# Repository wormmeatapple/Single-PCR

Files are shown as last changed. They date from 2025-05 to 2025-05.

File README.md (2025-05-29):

# Single-PCR
A cheap, easy to use single tube PCR thermocycler for biotech.
For Hack Club's Highway event!

<p>Polymerase-chain-reaction (PCR for short) is a vital reaction used in all sorts of biology fields. It amplifies a predetermined segment of dna, doubling it every cycle! PCR has three steps; 1. Get quite hot (95c) to split apart dna 2. Cool back down to allow little marker pieces of rna to anneal to the big, now detached dna 3. Heat back up to allow little protein machines to create more dna! This repeats 20-40 times until you have BILLIONS of copies of a specific piece of dna. This cycling is often done in very expensive, university level PCR thermocyclers that use peltier modules to heat and cool dynamically. My design does the same heating and cooling by using much cheaper components, resistive heaters and cpu fans. (Back in the day they used heated water baths!). I aim for Single-PCR to be a cheap easy PCR alternative for hobbyists. It'll be controlled by an ESP-8266 board broadcasting a control website. From the control website you can adjust cycles, monitor temperature data, abort reactions etc. Creating this vital piece of hardware would allow me to preform tons of different biohacking protocols, and if I can make it cheap enough, maybe it'll let others do the same!<p/>
  
singlepcr

|Item name|What the item is for in your project|Item source|Item price (include shipping + taxes)|Total price|
|--------|-------------------------------------|------------|-------------------------------------|------------|
|Aluminium heating block|To hold the PCR tube,and to be heated and cooled by the heating elements/cooling fans|JLCPCB CNC manufacturing|60.56+27.66 shipping|88.22|
|Heating element 2 pcs|To heat the heating block and thus the tube inside it.|https://www.aliexpress.com/item/1005007920697887.html?|2.92+9.36 shipping|12.28|
|10kΩ NTC Thermistor 10 pcs|To give temperature readings so the microcontroller knows when to heat/cool.|https://www.aliexpress.com/item/1005008177000786.html?|3.51+0 shipping|3.51|
|12V 1A wall-mounted DC power supply|Supply 12V power to the heaters and the fan.|https://www.aliexpress.com/item/1005005763465796.html?|5.08+0 shipping|5.08|
|Thermal paste|Increase thermal conductivity between heaters and heating block.|https://www.aliexpress.com/item/1005007037912738.html?|4.29+0 shipping|4.29|
|Transistors (12V)|Allow the microcontroller to control whether the fan gets power.|https://www.aliexpress.com/item/1005008370773690.html?|1.82+0 shipping|1.82|
|DC Fans 2 pcs|Blow air across the heatsink fins to cool down the heating block.|https://www.aliexpress.com/item/1005006306536871.html?|10.60+0 shipping|10.60|
|ESP control board|Read temperature data, control transistors, broadcast control website to user.|My cupboard|Free!I have some|0.00|
|**Total**||| |**125.80 AUS**/**80.60 USD**|

<br>
<br>





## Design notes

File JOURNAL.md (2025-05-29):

---
title: "Single-PCR"
author: "wormmeatapple"
description: "A tiny PCR machine designed to be cheap and easy"
created_at: "24th/5/2025"
time taken: 9 hours
---

## May 24th

> Created repo  
> Found the parts I'm going to need; heater elements and thermistors  
> Started 3d modelling based on selected parts



<p>I want to try and limit how much material is between the heaters and the tube, so I'm using a quite thin wall. I did ask people in the #cad channel what they thought of this but at time of writing I didn't get a reply</p>



<p>Heatsink fans on one side, now just to mirror them.</p>



<p>Very nice! We now have a hole for the PCR tube to go in, a hole for the thermistor, slots for the heaters and heatsinks to cool down easier. I'm not sure how well this'll be CNCed as I've never ordered a CNC part before but hopefully nothing breaks.</p>

> Time taken: about **30 mins**  
> - Modelling  
> - Researching parts

## Still May 24th

<p> Spent a ton of time researching and compiling parts. While not very technical, it's time that's very much needed. I also now know the specs of everything, so I can start writing code to control it all!</p>

> Time taken: **1 hour**
> - Compiling BOM
> - Researched all parts

## May 25th

>Started designing a wiring circuit

<p>First time ever using a pcb designer, but I'm slowly making process on the wiring schematic. I'm making it on easy-ada designer and since it technically isn't really a pcb alot of the parts I need aren't there.</p>
<p>This could maybe be a pcb? It'd be kinda small but it'd make wiring everything slightly easier? Something for me to think about.</p>
<p>Just as I was about to take a screenshot, website froze up and erased my progress. -__- I can't prove it either which sucks. Ah well, an hour wasted. Time for lunch.</p>

<br>



<p>Screenshotting more frequently this time.</p>



<p>Fans and thermistor circuit all wired up, now just the heaters.</p>



<p>Done! I'm sure I could of done it better, faster and with the proper parts, but for the first time designing a circuit like this I think I did alright. I'll send it into the highway chat and see if anyone finds an issue in it.</p>
<p>As soon as I wrote that I looked back on it and wanted to make a couple of changes, one second...</p>



<p>Much nicer. The old format made sense, but for someone who isn't as well versed in circuitry this is way easier to follow</p>

> Time taken **1h 57m**
> - Wired up all components
> - Lost an hour to a crash :sob:

<p>Got some feedback on my schematic. Mainly that I should wire the heaters in parellal and I should change the relay for a transistor.</p>



> Time taken **7m**
> - Finally learnt how to tell if something is parellal 

> Now time to code up the control side of everything
<p>My plan is to have a website that the esp8266 broadcasts and the user connects to. Once you've connected you can choose the cycle times and monitor the temperature.</p>



<p>Stupid port 6 only opens when I'm in device manager.</p>
<p>So weird, I keep getting a "permission denied" error for my com port?</p>
<p>Ohhhhh, having serial monitor open counts as a connection, so arduino ide wasn't free to flash. Everything is back to working now.</p>
<p>Just fiddled around with the code for a while before I realised it was trying to be a station not an access point. 🤦</p>



<p>Was going to take this screenshot to complaing about how it isn't working, but instead found my phone is just refusing to display the html. In other news, finally have a prototype! Now I can start drafting the other functions I need like reading temp and making a cycle.</p>

<p>Code now handles different links. Not exactly necessary as everything needed by the user is on the homepage, but is useful for AJAX (acting like I didn't learn what AJAX was today</p>

<p>Now a div in the html is updated every second with the readings from the thermistor using AJAX. Preferably I would like it to be graphed over time and overlayed on the user's requested cycle, but the only graphing option I've found relies on using an external JS libary.</p>



<p>So messy. I can't even read it.</p>

<p>That's it for today. All and all pretty efficient. Posting the arduino sketch right after I commit this.</p>

> Time taken **2h 27m**
> - Added webserver functions to controller
> - Added simple temperature function
> - AJAX to continously update page with temperature data
> - Started adding fan/heater control

## May 26th

<p>Just got three things left to do before I submit,</p>

> - Add graphing while offline
> - Add a way to specify cycles that the controller reads and then actually does
> - Overlay the temp graph and the cycle graph (probably easiest?)

<p>Gonna work on the graphing first. In my research I kept seeing people suggest the Chartly.JS library, but this doesn't work while offline. Hm</p>

<p>I think I've found a solution. I'm gonna install LittleFS on my board and than just store the js libary on my esp? I hope</p>

<p>Why won't the tool show up in the tool dropdown?</p>



<p>That's annoying. I've just spent ages (futilely) trying to get the uploader to show in the tool dropdown, but I just checked the size of chartly and it's more than the flash size. Awesome. I guess I'll have the board act as an AP and a STA so that it has wifi access. Booooo.</p>

<p>I'm deciding to temporarily put the graphing on hold and focus on the actual functionality of turning the heater and fan on and off to reach a desired temp.</p>

<p>Now that I'm making it, why is this thing website operated? It can't keep a substantial memory so it wouldn't be able to store preset cycles decided by the user or anything like that. I'll keep the webserver stuff for now, but when it's done it'll probably just be used to start the cycle and read the temp 👎</p>

<p>Actually no, the cycles will stay the same, but depending on the GC content of the dna being PCRed, denaturation has to change. So instead it'll be like a form where you input how long the denature and extension steps have to be. Honestly such a relief, I thought all my webserver shenanigans would be a waste.</p>

<p>Okay I've actually figured out a procedure that actually makes sense. When you boot up the machine you follow these steps. 1. Connect to the access point 2. Enter in your PCR settings like number of cycles, length of each phase, temp of each phase etc 3. Hit start 4. Watch the temp graph</p>



<p>I've added in a function to control the heat simply by polling the therm, if lower than the ideal heat turn on heaters, if higher turn on fans. Than I put it into the loop connected to an if statement that turns on when you submit the form of variables. All the durations and ideal temps are governed by the variables that you chose from the form. !!! It should all be good and working! Just need to fix up the html. Also sidenote I don't know the proper way to do it but why can't I just have this function be void. If it has any arguements has to return something like bruh.</p>

<p>Blank white screen on my arduino ide. Worrying.</p>

<p>Was able to press save despite the blank screen of nothing. Maybe I should make a backup...</p>



<p>Pretty simple cycle mechanic. I do wonder if the delays in the cycle() function will stop the handleclient() function from working. I guess we'll find out eventually</p>

<p>Tested out everything and it seems to work. Forms send info, info gets converted to variables, variables control cycle, cycle controls pins. I even got the pins to light up an led, so it should be all good to go! I do wonder if there's a cheaper way to get my heating block CNCed though. I'll ask highway.</p>

> Time taken
> - **3h 2m**
> - Rethought of project design
> - User data converted to cycle settings
> - cycle settings control pins

<p>Gonna submit it today, I'm scared that I'll be missing something really simple and have to wait a week before submitting again. I definitly could have made this quicker, but I always choose to do new things for these events, I suppose that's the point though.</p>

## May 29th

<p>Got some feedback from @alexren, so I thought I'd talk a little about how a typical PCR machine works in detail (I'll add a simplier version to the readme).</p>

<p>If you've read the readme of this project, you know a PCR machine's main goal is to just change the temperature of a little chemical reaction in a repeating nature. The thousand dollar ones found in universities and real labs use peltier modules, which is essentially an electric heat pump.</p>



<p>If you power it, one side gets cold and the other gets hot. Flip the polarities and the hot and cold sides switch. So, a good PCR machine has your standard heating block to allow smooth temp distribution, and then some high quality peltiers stuck to it, allowing you to switch between hot and cold preeeety quick. Now I'm not a university or million dollar biotech lab, so I've gotta use a different method. I have to do heating through a ceramic resistance based heater, and cooling through a fan and heatsink. This works fine, if slightly slower to reach the appropriate temps, because the temperature PCR occurs at is pretty warm anyway. All the fan is doing is reversing the heating process essentially. So my heater gets the heat block (and thus the PCR tube) hot, and then the fan cools it back down quicker than ambient heat loss would. There is technically one thing about a regular PCR machine that I can't emulate. Usually after a PCR reaction has finished cycling and done the final extension step, the peltiers cool it all the way down to around 4c. This is just to protect the dna since it's a pretty delicate molecule, and transforming a broken piece of dna into something is a bad idea. To combat this, if you use Single-PCR, just be there when the reaction finishes to move your dna into the freezer 👍.</p>

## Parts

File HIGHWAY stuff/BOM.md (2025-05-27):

> **Total = 81.13 AMERICAN DOLLARS**
> - 125.80 AUS

# Aluminium heating block 
<br> **60.56** + **27.66 shipping** <br> **88.22 total** If anyone knows any cheaper cnc options please contact me :sob:<br>
# Heating element 2pcs 
<br> **2.92** + **9.36 shipping** <br> **12.28 total** <br>
# 10k NTC Thermistor 10pcs 
<br> **3.51** + **0 shipping!!** <br> **3.51 total** <br>
# 12 volt 1 amp wall mounted DC power supply 
<br> **5.08** + **0 shipping!!** <br> **5.08 total** <br>
# Thermal paste 
<br> **4.29** + **0 shipping** <br> **4.29 total** <br>
# Transitors (12v) 
<br>  **1.82** + **0 shipping** <br> **1.82 total** <br>
# DC Fans 2pcs
<br> **10.60** + **0 shipping** <br> **10.60 total** <br>
# Esp control board
<br> **Free! I have some** 

<br>

<p>Prices in BOM in AUS</p>

[BOM.csv](https://github.com/user-attachments/files/20453770/BOM.csv)

<p>I wasn't sure what was meant by csv table, I hope this is okay...</p>

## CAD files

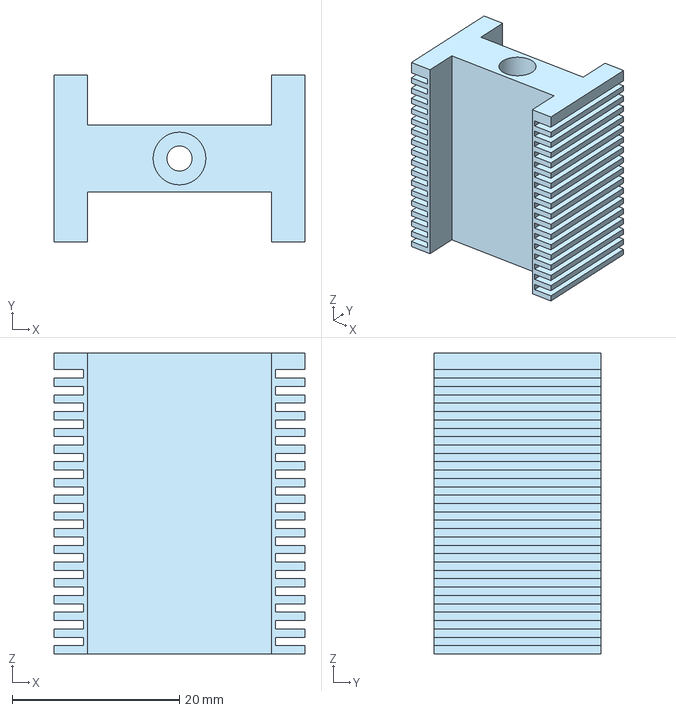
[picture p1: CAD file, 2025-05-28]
CAD stuff/singlepcrheatingblock.step
30.0 x 20.0 x 36.0 mm

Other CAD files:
singlepcrheatingblock.step
CAD stuff/singlepcrheatingblock.stl

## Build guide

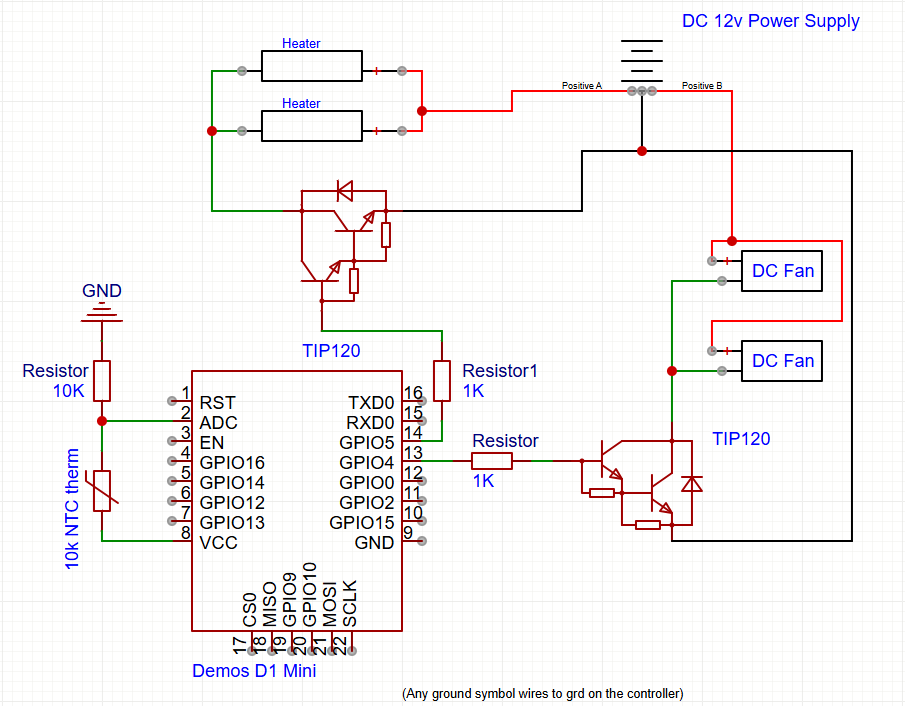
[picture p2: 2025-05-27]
WIRING stuff/wiringschematic.png

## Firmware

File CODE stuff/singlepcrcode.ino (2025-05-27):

#include <ESP8266WiFi.h>
#include <ESP8266WebServer.h>


//wifi variables
const char* ssid = "Single_PCR";
const char* password = "admin";
IPAddress local_ip(192,168,1,1);
IPAddress gateway(192,168,1,1);
IPAddress subnet(255,255,255,0);
ESP8266WebServer server(80); //port 80

//sensor variables
const int analogPin = A0;
const int resistorValue = 10000; //read therm res and change when it arrives

//pcr specific variables
bool on = false;
int extensionDur = 0;
int extensionTemp = 0;
int denatureDur = 0;
int annealDur = 0;
int annealTemp = 0;
int cycleNum = 0;


//temp control variables
const int heaterPin = D1;
const int fanPin = D2;

float read_temp()
{
  int sensorValue = analogRead(analogPin);
  float resistance = resistorValue / ((1023.0 / sensorValue) - 1.0);
  float temp = log(resistance / 10000.0) / 3950.0 + 1.0 / (25 + 273.15);
  return temp;
}

int cycle(int duration, int idealTemp)
{
  unsigned long startTime = millis();
  long elapsed = millis() - startTime;

  while (elapsed < duration)
  {
    float currentTemp = read_temp();
    if(currentTemp < idealTemp)
    {
      digitalWrite(heaterPin, HIGH);
      delay(100);
      digitalWrite(heaterPin, LOW);
    }
    else if (currentTemp > idealTemp)
    {
      digitalWrite(fanPin, HIGH);
      delay(100);
      digitalWrite(fanPin, LOW);
    }
    elapsed = millis() - startTime;
  }
  return 1;
}

//handle different links
void handle_connect()
{
  server.send(200, "text/html", SendHome());
}
void handle_data()
{
  float temp = read_temp();
  server.send(200, "text/html", String(temp));
}
void handle_start()
{
  on = true;

  if (server.hasArg("extensionDur")) {
    extensionDur = (server.arg("extensionDur").toInt()) * 10;
  }
  if (server.hasArg("extensionTemp")) {
    extensionTemp = (server.arg("extensionTemp").toInt()) * 10;
  }
  if (server.hasArg("denatureDur")) {
    denatureDur = (server.arg("denatureDur").toInt()) * 10;
  }
  if (server.hasArg("annealDur")) {
    annealDur = (server.arg("annealDur").toInt()) * 10;
  }
  if (server.hasArg("annealTemp")) {
    annealTemp = (server.arg("annealTemp").toInt()) * 10;
  }
  if (server.hasArg("cycleNum")) {
    cycleNum = server.arg("cycleNum").toInt();
  }

}
void handle_404()
{
  server.send(404, "text/html", "Send a real link dingus");
}

void setup()
{
  Serial.begin(115200);
  Serial.println();

  WiFi.softAP(ssid, password);
  WiFi.softAPConfig(local_ip, gateway, subnet);
 
  //link directory
  server.on("/", handle_connect);
  server.on("/data", handle_data);
  server.on("/start", handle_start);
  server.onNotFound(handle_404);

  server.begin();
  Serial.println("we bootin");

  pinMode(heaterPin, OUTPUT);
  pinMode(fanPin, OUTPUT);
}

void loop()
{
  server.handleClient();

  if(on)
  {
    cycle(300, 95); //inital denature
    for(int i = 0; i < cycleNum + 1; i++)
    {
      cycle(denatureDur, 95); //cycle denaturing
      cycle(annealDur, annealTemp); //cycle annealing
      cycle(extensionDur, extensionTemp); //cycle extension
    }
    cycle(300000, extensionTemp); //final extension
    on = false;
  }
}

String SendHome()
{
String html = "<!DOCTYPE html> <html>\n";
  html +="<head><meta name=\"viewport\" content=\"width=device-width, initial-scale=1.0, user-scalable=no\">\n";
  html +="<title>Single PCR</title>\n";
  html +="<style>html { font-family: Helvetica; display: inline-block; margin: 0px auto; text-align: center;}\n";
  html +="body{margin-top: 50px;} h1 {color: #444444;margin: 50px auto 30px;} h3 {color: #444444;margin-bottom: 50px;}\n";
  html +="</style>\n";
  html +="</head>\n";
  html +="<body>\n";
  html +="<h1>Single PCR</h1>\n";
  html +="<h3>Rancid inc. Making things Rancid since 1893</h3>\n";
  html +="<form action='/start'>";
  html +="Duration of extension: <input type='text' name='extensionDur'><br>";
  html +="Temperature of extension: <input type='text' name='extensionTemp'><br>";
  html +="Duration of denaturing: <input type='text' name='denatureDur'><br>";
  html +="Duration of annealing: <input type='text' name='annealDur'><br>";
  html +="Temperatur of annealing: <input type='text' name='annealTemp'><br>";
  html +="Amount of cycles: <input type='number' name='cycleNum'><br>";
  html +="<input type='submit' value='Submit'>";
  html +="</form>";
  html +="</body>\n";
  html +="</html>\n";
  return html;
}

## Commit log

2025-05-24 Modelled heating block
    Researched parts and modelled heating block for tube to go in.
2025-05-24 storing heatingblock file here
    [singlepcrheatingblock.step]
2025-05-25 added the wiring schematic
2025-05-27 updated wiring schematic
2025-05-28 organised everything awesome
    [singlepcrheatingblock.step, singlepcrheatingblock.stl]
